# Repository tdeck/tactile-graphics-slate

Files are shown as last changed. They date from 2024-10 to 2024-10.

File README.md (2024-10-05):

# Pixel Art Slate

The Pixel Art Slate is an experimental tool for creating tactile graphics that can be used by both Blind and sighted people. Inspired by the graphical medium of pixel art, it is a compact 3D printable frame that fits a standard 3x5 index card.

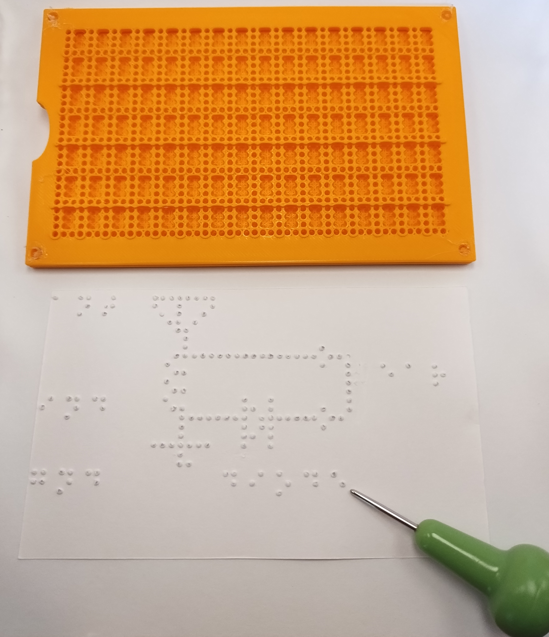
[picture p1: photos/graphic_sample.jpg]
Slate showing tactile graphic embossed on a 3x5 card, with typical braille stylus


A typical braille slate enables a Blind user to write braille and provides guides for properly spaced characters. This design is simple, portable, and had endured for 200 years. However, it doesn't allow you to create continuous lines of dots because of the blank spaces in between character positions. The Pixel Art Slate extends this basic design; it has the familiar "open" six dot cell positions, but also has a column of single dots that can be embossed between each braille cell. This means you can create unbroken shapes and filled areas of different sizes in addition to braille.

The Pixel Art Slate also has features to help you lay out your drawings and keep track of your location. There is a circular raised bump at the "intersection" of each braille cell position (that is, the dot that is in between both a row of braille and a column of braille). There is a raised ridge between every 2 braille lines, just like a standard slate. And there is a set of 3D printable markers. These markers are small tactile elements with pegs that can be temporarily inserted into the holes of the slate to mark out positions. There are long bar-shaped markers for creating lines and marking out space, and smaller arrow and L-shaped markers. Of course, you can always pull out your drawing-in-progress from the slate to check it and the markers will remain in place.

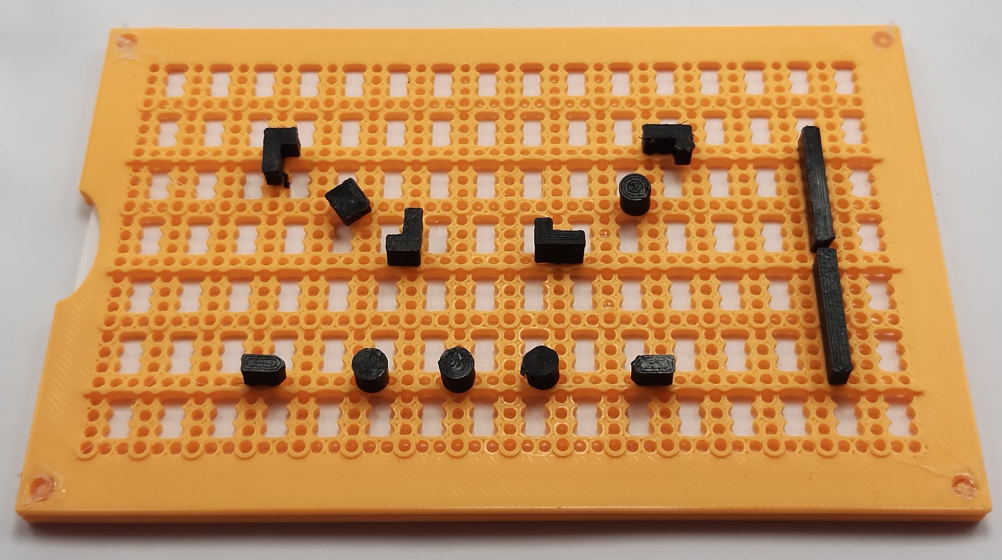
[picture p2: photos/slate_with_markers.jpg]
Slate an assortment of attached markers


The slate was designed in OpenSCAD, making it easy to tweak it or create a larger version. See https://github.com/tdeck/tactile-graphics-slate

## Printing

Files are in the prints folder.

Both parts should be printed in their provided orientation. The base should be printed with fine layer heights (e.g. .1mm) so that the hemisphere depressions for each dot will have the right shape. The cover and markers are less sensitive to layer height.

This is a large flat print so warping is a significant concern. You'll need good bed adhesion to print this properly.

PLA works just fine for this print.

I recommend printing a bunch of duplicate markers because they're small and easy to lose, and somewhat fragile. They take almost no plastic and very little time to print.

## Assembly

The slate is designed to be printed in two parts, then permanently joined. There are 4 pegs at each corner of the cover, and 4 corresponding holes in the cover. Once the cover has been placed on these pegs, you should be able to slide in a 3x5 card into the slot on the side. You can permanently join the top and bottom halves with glue around the edges, or by heating up and pressing down the 4 protruding pegs so they form a kind of plastic rivet.

## Code
The code is all in slate.scad and can be adapted for different sizes of slates. I haven't modeled a hinge, but by making the alignment pegs smaller and increasing the clearance the pegs can be made to punch through paper and hold a slate in place. If you want to use the slate this way, disable the card cutout option.

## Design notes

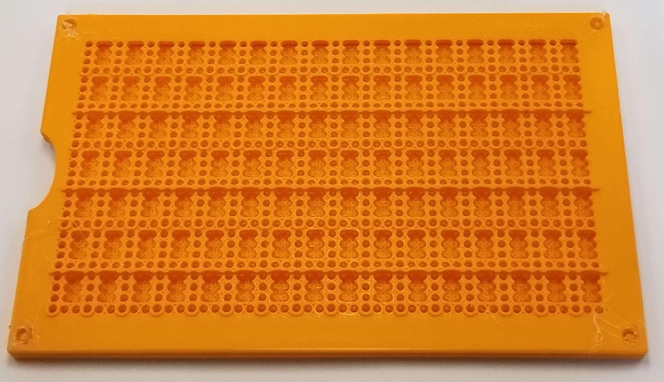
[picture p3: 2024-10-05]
photos/slate_empty.jpg

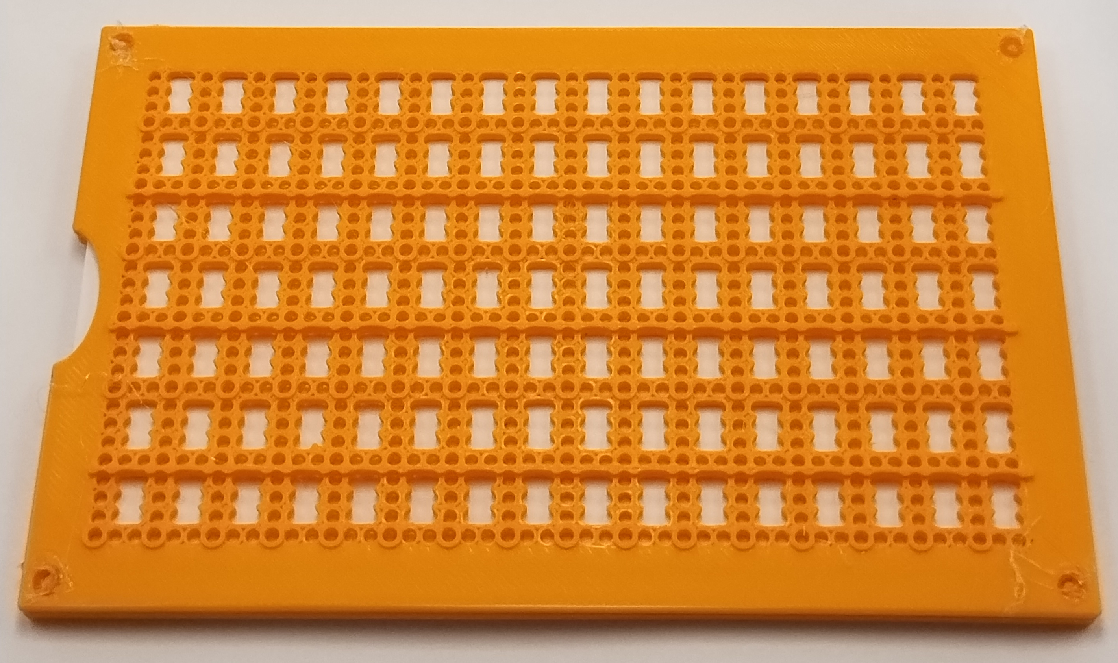
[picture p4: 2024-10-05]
photos/slate_full.jpg

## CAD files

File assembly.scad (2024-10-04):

include <slate.scad>;
$part = "none";
// This imports the rendered STLs and assembles them because they're so complex they break the preview
// and take ages to render

import("prints/3x5_base.stl");
up(BASE_THICKNESS) import("prints/3x5_cover.stl");

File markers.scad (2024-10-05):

include <slate.scad>;
$part = "none";

PEG_HEIGHT = TOP_THICKNESS + LINE_RIDGE_HEIGHT;
PEG_CLEARANCE = .22; // To allow the peg to be inserted; radius clearance
PEG_DIAM = hole_diameter - 2 * PEG_CLEARANCE;
PEG_END_CHAMFER = .2; // To make the peg easier to insert
PEG_BASE_CHAMFER = .4; // To help keep the peg from snapping off
BASE_THICKNESS = 5;

module peg() {
    // Flat on the horizontal plane, pointing up
    cyl(
        d=PEG_DIAM,
        h=PEG_HEIGHT,
        align=V_UP,
        orient=ORIENT_Z,
        chamfer2=PEG_END_CHAMFER
    );
    
    // Base chamfer
    cyl(
        d1=PEG_DIAM + 2*PEG_BASE_CHAMFER,
        d2=PEG_DIAM,
        h=PEG_BASE_CHAMFER,
        align=V_UP,
        orient=ORIENT_Z
    );
}

module peg_pair() {
    // Flat on the horizontal plane, pointing up
    left(DOT_SPACING / 2) peg();
    right(DOT_SPACING / 2) peg();
}

module arrow_marker() {
    // 2 peg directional marker with an arrow end
    // This is printed upside down so there isn't support around the delicate pegs
    // Flat on the horizontal plane pointing up
    marker_width = DOT_SPACING;
    
    cuboid([5, marker_width, BASE_THICKNESS], align=V_DOWN);
    
    // here we have to use the pythagorean theorem!
    triangle_leg = sqrt(marker_width*marker_width / 2);
    
    left(2.5)
    zrot(-45)
        right_triangle(
            [triangle_leg, triangle_leg, BASE_THICKNESS],
            orient=ORIENT_Z,
            align=V_DOWN
    );
   
    peg_pair();
}

module corner_marker() {
    // 2 peg directional marker with an L-shape
    
    cuboid([3*DOT_SPACING, DOT_SPACING, BASE_THICKNESS], align=V_DOWN + V_BACK);
    
    left(3/2*DOT_SPACING)
    cuboid(
        [DOT_SPACING, DOT_SPACING, BASE_THICKNESS],
            align=V_DOWN + V_FWD + V_RIGHT);
    
    back(DOT_SPACING/2)
    right(DOT_SPACING/2) peg_pair();
}
    

module circle_marker() {
    // 1 peg non-directional marker
    diam = 5;
    
    zcyl(h=BASE_THICKNESS, d=diam, align=V_DOWN);
    peg();
}

module square_marker() {
    // 1 peg non-directional marker
    downcube([5, 5, BASE_THICKNESS]);
    peg();
}

module eight_peg_line_marker() {
    cuboid(
        [DOT_SPACING, 8*DOT_SPACING, BASE_THICKNESS],
        align=V_DOWN + V_FWD
    );
    for (i = [0:7]) {
        forward(DOT_SPACING * (i + .5)) peg();
    }
}

eight_peg_line_marker();
right(10) arrow_marker();
right(20) corner_marker();
right(30) circle_marker();
right(40) square_marker();

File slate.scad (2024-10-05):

include <BOSL/constants.scad>;
use <BOSL/transforms.scad>;
use <BOSL/shapes.scad>;


// 3x5 card
USE_CARD_CUTOUT = true;
ROWS = 28;
COLUMNS = 48;

CARD_CUTOUT_WIDTH = 5 * 25.4 + 3;
CARD_CUTOUT_LENGTH = 3 * 25.4 + 1;


/*
// Small test piece
USE_CARD_CUTOUT = true;
ROWS = 8;
COLUMNS = 8;
CARD_CUTOUT_WIDTH = 28;
CARD_CUTOUT_LENGTH = 26;
*/

DOT_SPACING = 2.54; // This is the CA sign standard where the cell spacing is a multiple of dot spacing
DEPRESSION_DIAMETER = 1.9;
DEPRESSION_DEPTH = .7; // TODO maybe this should be shallower
STYLUS_GUIDE_CLEARANCE = .1;

BASE_THICKNESS = 3;
TOP_THICKNESS = 2;
SIDE_SPACE = 7;
CHAMFER_HEIGHT = .4; // This makes it easier to remove the print from the bed

CARD_CUTOUT_THICKNESS = .9; // Don't want this to flatten the dot
CARD_FINGER_NOTCH_SIZE = 20;
CARD_FINGER_NOTCH_DEPTH = SIDE_SPACE - .8;

/* For reclosable
ALIGNMENT_SPIKE_TOP_DIAM = .5;
ALIGNMENT_SPIKE_BOTTOM_DIAM = 1.5;
ALIGNMENT_SPIKE_HEIGHT = 3;
ALIGNMENT_HOLE_CLEARANCE = .3;
*/

// For welding
ALIGNMENT_SPIKE_TOP_DIAM = 2;
ALIGNMENT_SPIKE_BOTTOM_DIAM = 2.5;
ALIGNMENT_SPIKE_HEIGHT = 3;
ALIGNMENT_HOLE_CLEARANCE = .5;

USE_CELL_GUIDES = true;

RIDGE_SPACING = 8;
LINE_RIDGE_HEIGHT = 1; // These are every 8 dots (2 Braille lines)
COL_RIDGE_HEIGHT = 0; // These are every 8 columns, to match the above
MAX_RIDGE_WIDTH = 1.5; // These ridges will mostly be pierced by holes
INTERSECTION_BUMP_HEIGHT = 1;
INTERSECTION_BUMP_DIAM = DEPRESSION_DIAMETER + 2 * .8;

// Utility constants
ARBITRARY = 1000; // Arbitrary size for various hole dimensions
SMALL_DELTA = .01; // Small movement to resolve ambiguity when part edges overlap

 // Set global params for smoother shapes
$fa = 1;
$fs = .2;

plate_length = ROWS * DOT_SPACING + DEPRESSION_DIAMETER + 2 * SIDE_SPACE;
plate_width = COLUMNS * DOT_SPACING + DEPRESSION_DIAMETER + 2 * SIDE_SPACE;
hole_diameter = DEPRESSION_DIAMETER + 2*STYLUS_GUIDE_CLEARANCE; // Used in markers

module depression() {
    // Cut off top half to hopefully reduce work done in rendering
    difference() {
        zscale(2*DEPRESSION_DEPTH/DEPRESSION_DIAMETER)
            sphere(d=DEPRESSION_DIAMETER);

        up(2*SMALL_DELTA)
            upcube(ARBITRARY);
    }
}

module alignment_spike() {
    zcyl(
        d2=ALIGNMENT_SPIKE_TOP_DIAM,
        d1=ALIGNMENT_SPIKE_BOTTOM_DIAM,
        h=ALIGNMENT_SPIKE_HEIGHT,
        align=V_UP
    );
}

module card_finger_notch_carveout() {
    forward(plate_length / 2)
    scale([CARD_FINGER_NOTCH_DEPTH, CARD_FINGER_NOTCH_SIZE/ 2, 1])
        zcyl(h=ARBITRARY, r=1);
}

module bottom_plate() {
    difference() {
        cuboid(
            [plate_width, plate_length, BASE_THICKNESS],
            align=V_DOWN + V_RIGHT + V_FWD,
            chamfer=CHAMFER_HEIGHT
        );

        right(DEPRESSION_DIAMETER + SIDE_SPACE)
        forward(DEPRESSION_DIAMETER + SIDE_SPACE)
        down(USE_CARD_CUTOUT ? CARD_CUTOUT_THICKNESS: 0)
        for (r = [0:ROWS-1]) {
            for (c = [0:COLUMNS-1]) {
                right(c * DOT_SPACING)
                    forward(r * DOT_SPACING)
                        depression();
            }
       }

        // Card cutout (may be zero)
       if (USE_CARD_CUTOUT) {
            up(SMALL_DELTA)
                forward(plate_length / 2)
                cuboid(
                    [CARD_CUTOUT_WIDTH, CARD_CUTOUT_LENGTH, CARD_CUTOUT_THICKNESS],
                    align=V_DOWN + V_RIGHT
                );

           card_finger_notch_carveout();
       }
    }

    // Back alignment spikes
    spike_offset = SIDE_SPACE / 2;
    forward(spike_offset) {
        right(spike_offset) alignment_spike();
        right(plate_width - spike_offset) alignment_spike();
    }

    forward(plate_length - spike_offset) {
        right(spike_offset) alignment_spike();
        right(plate_width - spike_offset) alignment_spike();
    }
}

module alignment_hole_carveout() {
    zcyl(h=ARBITRARY, d=ALIGNMENT_SPIKE_BOTTOM_DIAM + 2*ALIGNMENT_HOLE_CLEARANCE);
}

module top_plate() {
    difference() {
        union() {
            cuboid(
                [plate_width, plate_length, TOP_THICKNESS],
                align=V_DOWN + V_RIGHT + V_FWD,
                chamfer=CHAMFER_HEIGHT
            );

            // Ridges
            color("green")
            right(SIDE_SPACE)  forward(SIDE_SPACE) {
                // Horizontal ridges
                for (r = [RIDGE_SPACING: RIDGE_SPACING: ROWS - 1]) {
                    forward(DEPRESSION_DIAMETER + r * DOT_SPACING - DOT_SPACING/2)
                        cuboid(
                            [plate_width - 2*SIDE_SPACE, MAX_RIDGE_WIDTH, LINE_RIDGE_HEIGHT],
                            align=V_UP + V_RIGHT
                        );
                }

                // Vertical ridges
                for (c = [RIDGE_SPACING: RIDGE_SPACING: COLUMNS - 1]) { // TODO these should start at right
                    right(DEPRESSION_DIAMETER + c * DOT_SPACING - DOT_SPACING/2)
                        cuboid([MAX_RIDGE_WIDTH, plate_length - 2*SIDE_SPACE, COL_RIDGE_HEIGHT],
                            align=V_UP + V_FWD
                        );
                }

                // Intersection bumps
                color("blue")
                for (r = [3: 4: ROWS - 1]) {
                    for (c = [COLUMNS - 3: -3: 0]) {
                        forward(DEPRESSION_DIAMETER + r * DOT_SPACING )
                            right(DEPRESSION_DIAMETER + c * DOT_SPACING)
                            zcyl(d=INTERSECTION_BUMP_DIAM, h=INTERSECTION_BUMP_HEIGHT);
                    }
                }
            }
        }

        right(DEPRESSION_DIAMETER + SIDE_SPACE) forward(DEPRESSION_DIAMETER + SIDE_SPACE) {
            for (r = [0:ROWS-1]) {
                for (c = [0:COLUMNS-1]) {
                    right(c * DOT_SPACING)
                        forward(r * DOT_SPACING)
                           zcyl(h=ARBITRARY, d=hole_diameter);
                }
           }

           // Center cutouts to indicate Braille cells
           if (USE_CELL_GUIDES) {
               for (r = [0: 4: ROWS - 3]) {
                   for (c = [COLUMNS -2: -3: 0]) { // TODO
                        right(c * DOT_SPACING)
                            forward(r * DOT_SPACING - hole_diameter/2)
                                cuboid([DOT_SPACING, 2*DOT_SPACING + hole_diameter, ARBITRARY], align=V_RIGHT + V_FWD);
                   }
               }
           }
       }

        // Alignment holes
        spike_offset = SIDE_SPACE / 2;
        forward(spike_offset) {
            right(spike_offset) alignment_hole_carveout();
            right(plate_width - spike_offset) alignment_hole_carveout();
        }

        forward(plate_length - spike_offset) {
            right(spike_offset) alignment_hole_carveout();
            right(plate_width - spike_offset) alignment_hole_carveout();
        }

        // Finger notch
       if (USE_CARD_CUTOUT) card_finger_notch_carveout();
    }
}

module geometry() {
    echo("Rendering part", $part);
    if ($part == "base") {
        bottom_plate();
    }

    if  ($part == "cover") {
        down(BASE_THICKNESS - TOP_THICKNESS) // Cura won't lay 2 parts in same STL on bed
            top_plate();
    }
}

geometry();

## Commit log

2024-08-24 Working test with letter cells
    Tested with card stok and it works, although there's no hinge so the
    initial attachment is difficult.
    [slate.scad]
2024-08-24 Lots of improvements
    - Guides aligned to right
    - Card cutout
    - Intersection bump
    [slate.scad]
2024-08-24 Fix + finger notch
    [slate.scad]
2024-09-06 3x5 version
    [slate.scad]
2024-09-06 Add assembly mode which won't preview because of CSG tree size
    [slate.scad]
2024-10-04 Significant tweaks + improvements + markers
    [assembly.scad, markers.scad, slate.scad]
2024-10-05 Ready to post to 3d sites
    [markers.scad, slate.scad]
